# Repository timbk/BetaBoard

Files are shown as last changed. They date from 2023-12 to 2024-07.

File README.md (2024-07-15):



# BetaBoard

A particle detector built for cost-effectiveness when ordered at O(100) pieces.

The detector concept is adapted from the [DIY Particle Detector Project](https://github.com/ozel/DIY_particle_detector) by Oliver Keller.

## Hardware Revisions

| Revision 1 | Revision 2 |
| :---: | :---: |
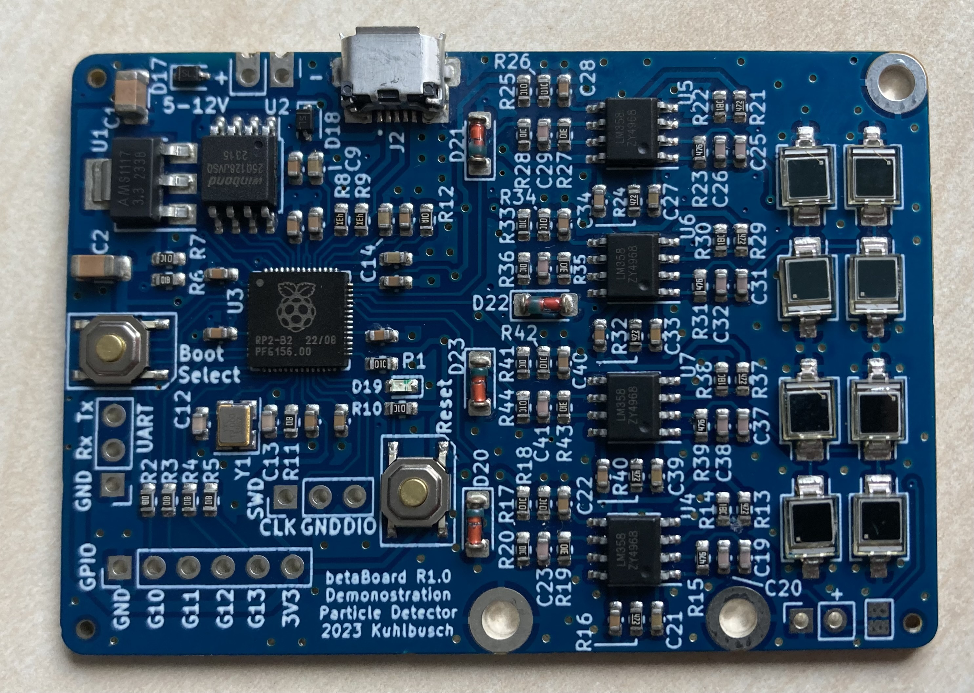
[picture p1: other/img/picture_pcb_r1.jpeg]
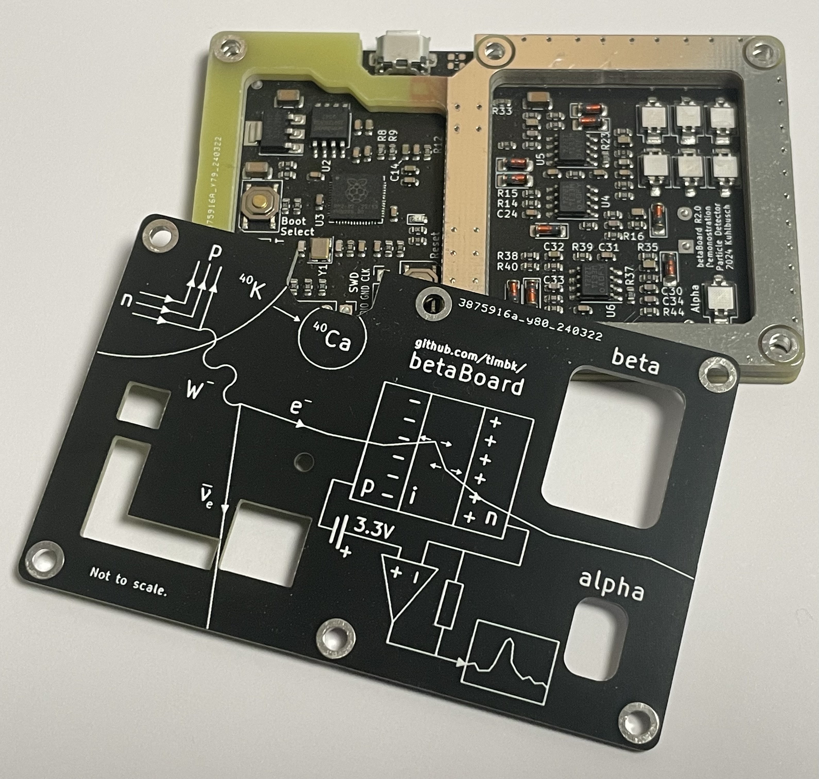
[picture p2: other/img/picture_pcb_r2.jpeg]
|  |  |
| [Schematic](hardware/betaBoard_r1.0/pdf/betaBoard_sch.pdf) [Layout](hardware/betaBoard_r1.0/pdf/betaBoard_pdf.pdf) | [Schematic](hardware/betaBoard_r2.0/betaBoard_r2.0_sch.pdf) [Layout](hardware/betaBoard_r2.0/betaBoard_r2.0_pcb.pdf) [Component Positions](hardware/betaBoard_r2.0/betaBoard_r2.0_positions.pdf) |
| Initial protoype: Working with adjustemtns to a few component values. Requires a lot of electrical and conductive tape to assemble. Designed for 16 diodes with the option to measure coincidences. | Streamlined redesign. Mainly adding a PCB casing to block light and radio imission. Attempting to add a simple alpha particle detector channel by stripping the isolation off of a diode (not successfull yet). Single channel with 6 diodes in parallel. Using additional ADC channels with less gain for debugging and potential experiments with scintillators. |

## Experiment Ideas

* Time distribution of pulses
* Rate vs distance (1/d^2 + offset)
* Absorption coefficient
    * Increase material thickness between detector and source
* Spectroscopy?? (alphas, sand down diode?
* Balloon in cellar

## Serial interface

* `T` `T <block_index> <timestamp_us> <overflow> # <sample_0> <sample_1> .. <sample_N>`
    * `block_index`: uint16_t, mainly relevant for debugging
    * `timestamp_us`: uint64_t, Trigger point timestamp in micro seconds since start of the measurement
    * `overflow`: bool, set to 1 if an overflow happend prior to this sample
    * `sample_n`:  int16_t, samples from the triggered waveform

## PCB

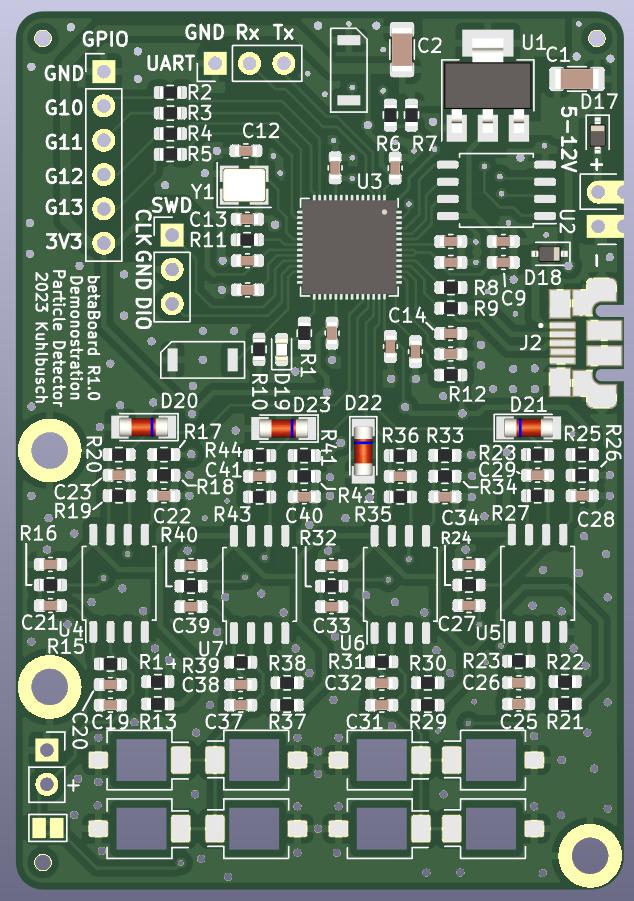
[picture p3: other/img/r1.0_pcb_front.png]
PCB front view

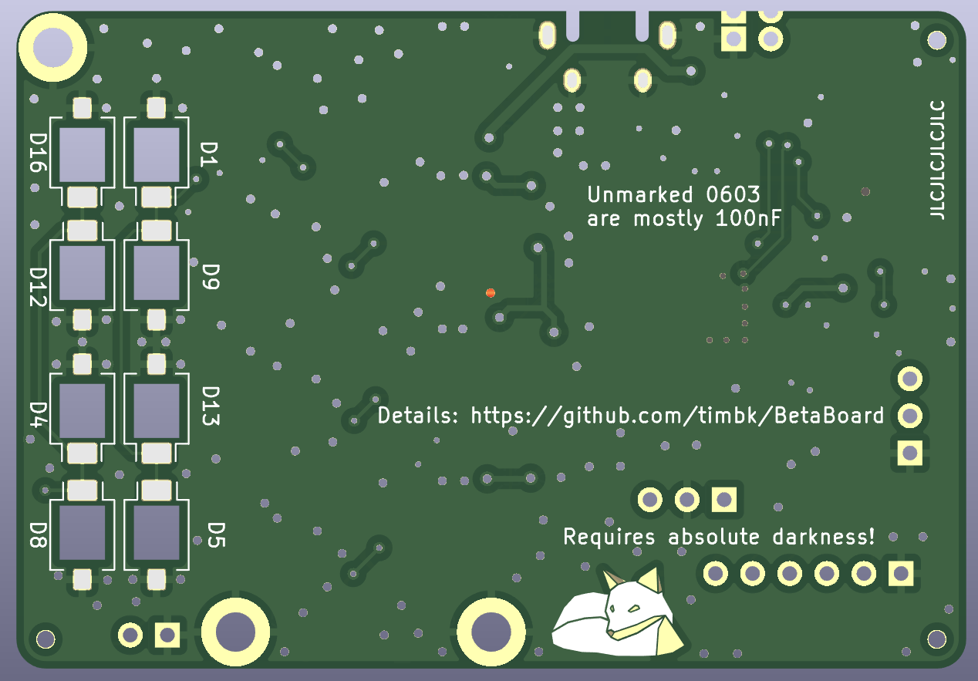
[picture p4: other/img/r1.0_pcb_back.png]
PCB back view


[Schematic](betaBoard/pdf/betaBoard_sch.pdf)
[Layout](betaBoard/pdf/betaBoard_pdf.pdf)

The goal was to keep it small to keep the PCB cost low and to make it fit easily.
Components were chosen to keep the price low and based on availablility at the chosen manufacturer.

## Ideas

* Strip detector with 4 pixels?
* File down SMD LEDs for less absorption?
* 3D-Printed Case?
* Interconnect multiple detectors?

## R2.0 ideas

* Put VCC on interconnect instead of 3V3
* Review diode cutout size
* Increase power supply castellated hole distance
* Increase LDO heat sink plane size
* Think about how usefull the coincidence concept is: 2x2 = 2+2 = 4!
* Silk to highlight Diode grouping
* Seperate bulk capacitor on 5V rail for analog

## Noise calculations

* Spice simulation: peak of ca. 40 $\mu\text{V}/\sqrt{\text{Hz}}$
    * Resistor thermal noise: $\sqrt{4k_BTR}\approx 400 ~ \text{nV/}\sqrt{\text{Hz}}$
    * LM358 input noise is ca. 40 $\text{nV}/\sqrt{\text{Hz}}$
    * Gain of second stage is ca. 100 for the peak frequency
    * => Resistor thermal noise is dominant part in simulation, LM385 noise should be negligible
        * $100 \cdot 400~\text{nV}/\sqrt{\text{Hz}} \approx 40~\mu\text{V}/\sqrt{\text{Hz}}$

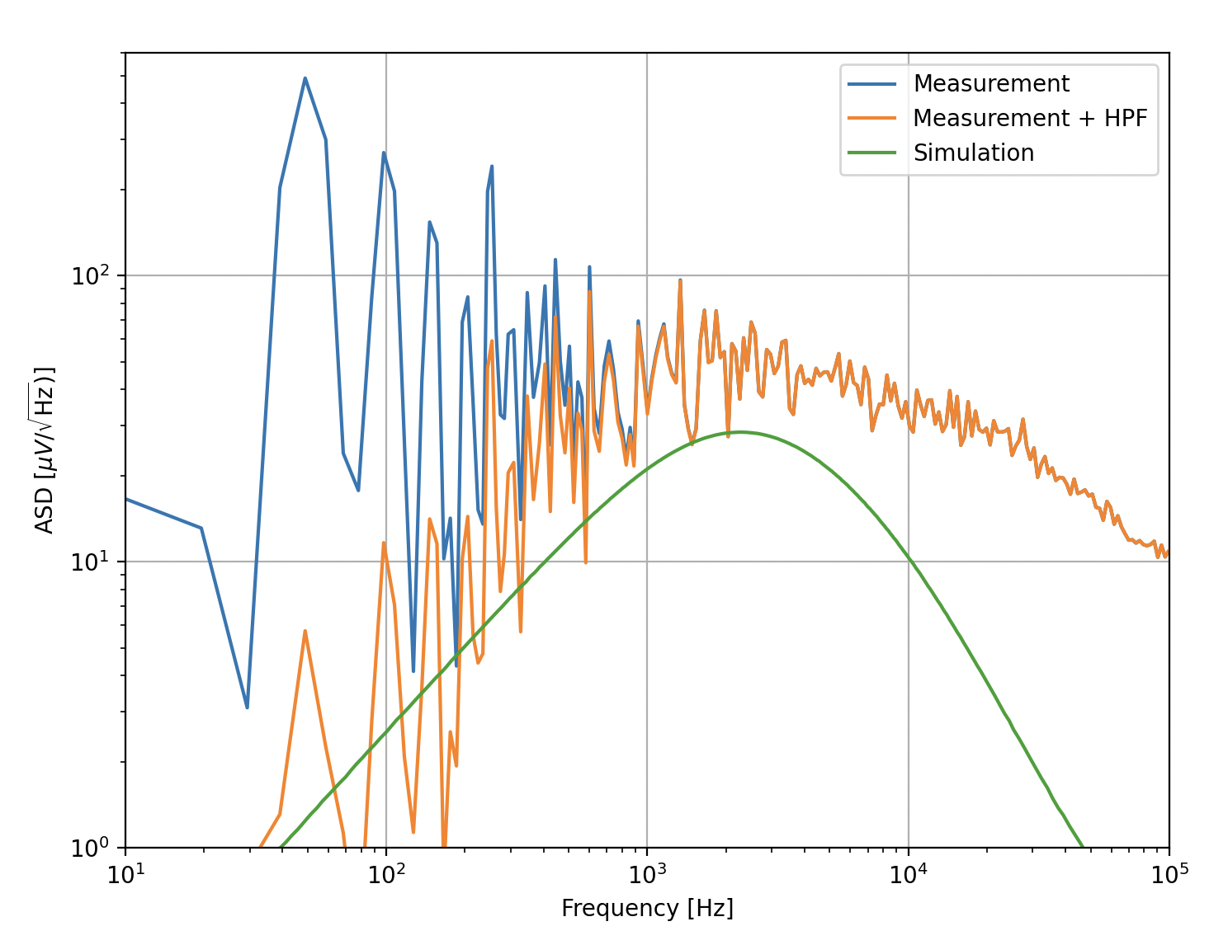
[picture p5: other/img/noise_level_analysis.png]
Noise plot


## Potential signal sources

* 10g KCl has ca. 164 Bq.
* Estimate of geometric acceptency at 2 cm distance: $A = \frac{4 \cdot 7.5~\text{mm}^2} {4\pi\cdot (20~\text{mm})^2} \approx 0.006$
    * With perfect efficiency: ca. 1 Hz

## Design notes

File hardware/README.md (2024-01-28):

# Hardware Files

## betaBoard.pretty

Custom KiCad footprints.

## betaBoard_r1.0

First revision of the PCB.

Design concepts:
* 4 Channels
    * adding channles came without significant cost (only opamps and passives)
    * 2 Channel on the back are expensive to populate
* Header to connect PD with leads
* External power header for up to 12 V to increase diode bias
* RP2040 allows simple programming via USB
    * Can be done by the user without special tools
* Allow options for different diode placement
    * More diodes yield more sensitivity

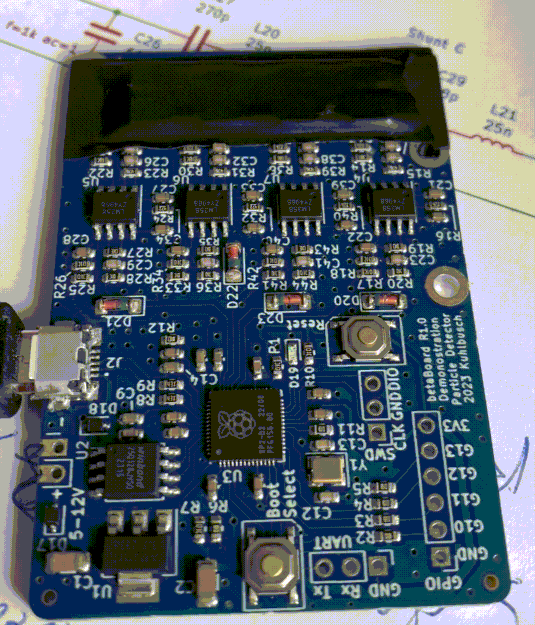
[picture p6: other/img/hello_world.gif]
PCB first LED blinking


Good:
* MCU, buttons, USB etc work perfectly out of the box :D

Challenges:
* High USB noise (1kHz spikes)
    * R14 requires a parallel C to get rid of noise from USB line
        * 1uF seems to help but does not seem sufficient (Could try 10uF, have 0603)
        * could increase R by factor 10
    * Try larger bulk capacitance (100uF or 1000uF)
        * 1000 uF seems to help!
        * Might be change in current draw
        * Cable length (resistance) seems to have an effect
    * Useing seperate diodes for the two supplies could help (diode voltage drop might depend on current)
    * TODO: Try if battery operation is better (helps to exclude potential points where 1 kHz noise couples)
* Is 40 MOhm working with the input impedance of LM358??
* Cut up groundplane at the PDs is probably not optimal
* Keep loop areas even smaller (I don't think it's the source of issues, but would feel better)
* USB port shielding is connected to GND. This might not be the optimal solution
    * Next: Add 2 0603 footprints? (allows open, short, 1MOhm+C)

## betaBoard_r1.1

Next revision. Work in progress.

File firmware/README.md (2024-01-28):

# RP2040 Firmware

## Build instructions

Requires a working installation of the [pico sdk](https://github.com/raspberrypi/pico-sdk).

```bash
cd firmware/
./build.sh
```

## Flashing

* Option 1: (simple)
> Hold the boot select pin on the PCB while connecting the board via USB. It will show up as a mass storage device. Copy `firmware/build/betaBoard.uf2` with a file manager (Finder/Explorer/..).

* Option 2: (complicated, but better for developement)
> Use a `picoprobe` and connect it to the SWD header. Execute the `./flash.sh` script.

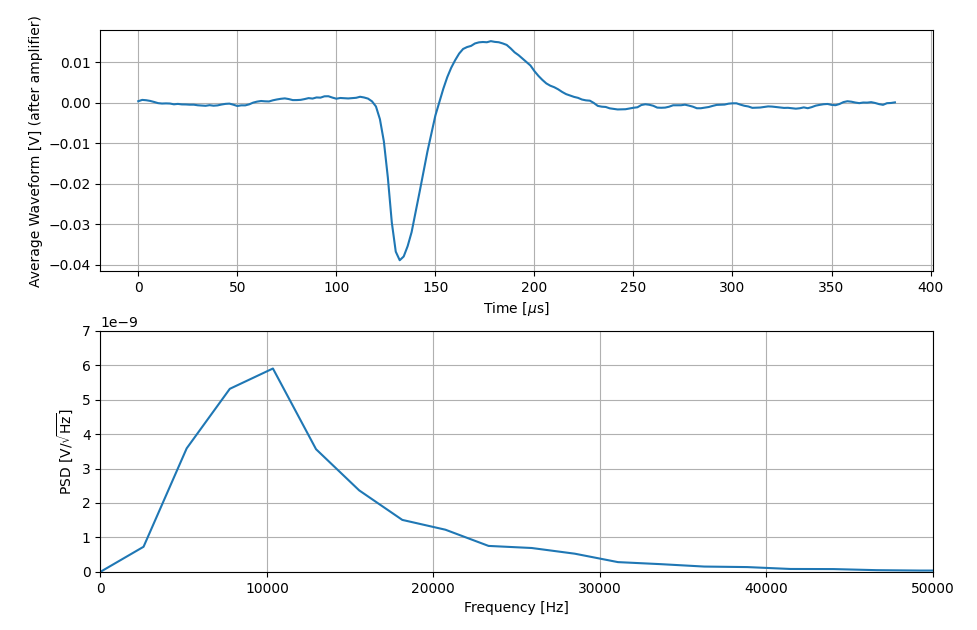
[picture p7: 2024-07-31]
other/img/avg_pulse_and_spectrum.png

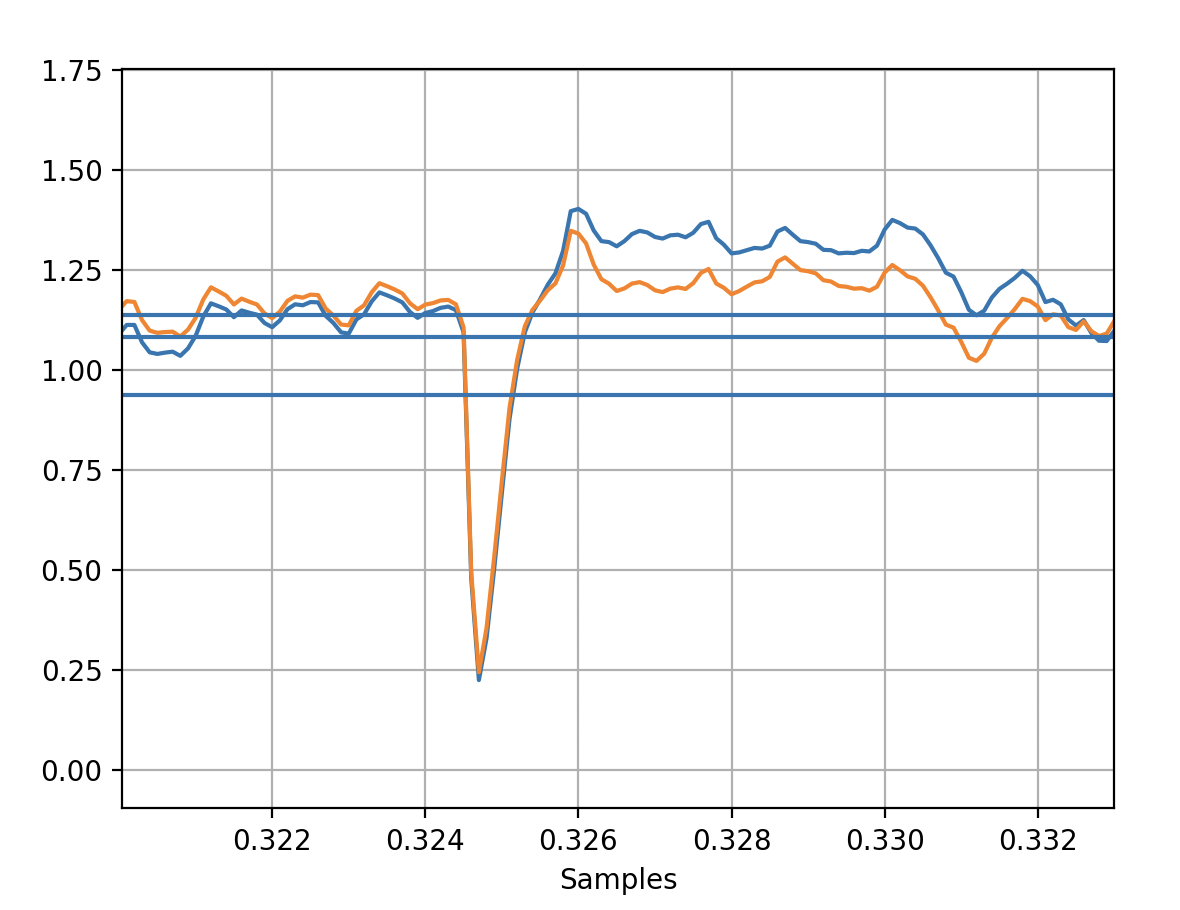
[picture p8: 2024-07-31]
other/img/first_pulse_maybe.png

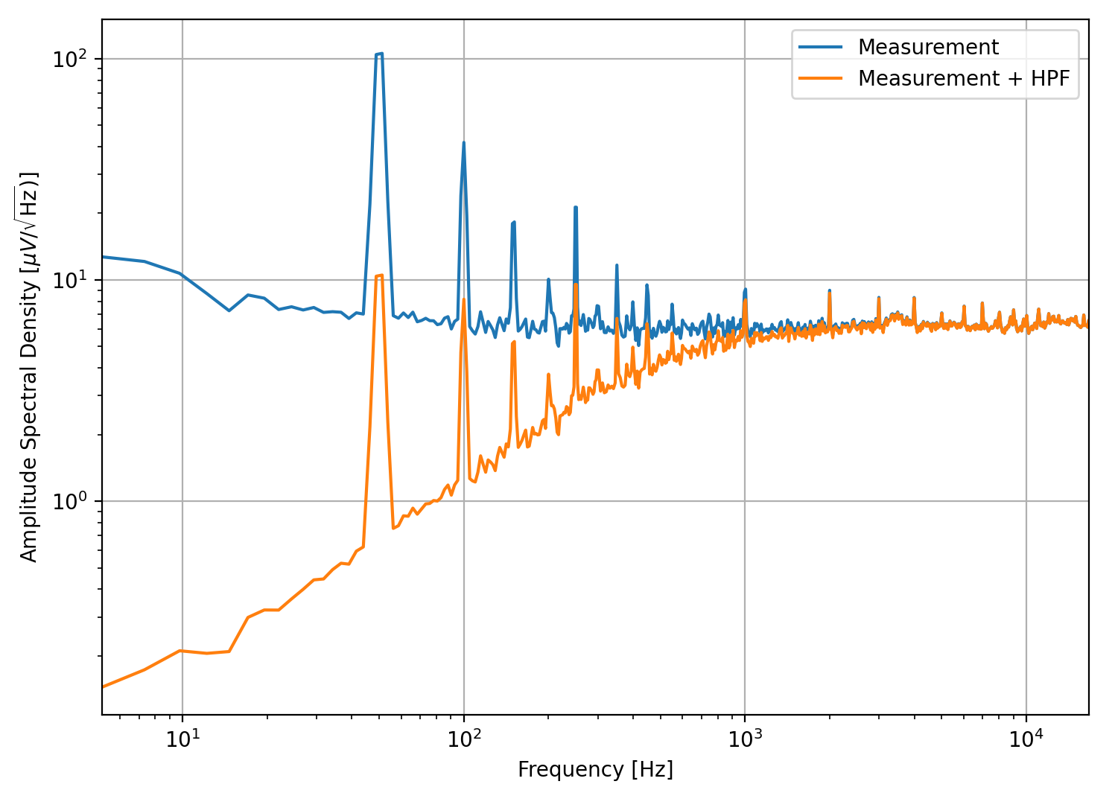
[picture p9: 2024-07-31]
other/img/noise_lpf.png

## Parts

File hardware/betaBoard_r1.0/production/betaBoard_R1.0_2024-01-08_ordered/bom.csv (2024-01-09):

Designator | Footprint | Quantity | Value | LCSC Part #
C1, C2 | 1206 | 2 | 10u
C10, C11, C15, C16, C18, C22, C24, C28, C3, C30, C34, C36, C4, C40, C5, C6, C7, C8 | 0603 | 18 | 100n
C12, C13 | 0603 | 2 | 30p
C14, C17, C9 | 0603 | 3 | 1u
C19, C20, C25, C26, C31, C32, C37, C38 | 0603 | 8 | 10p
C21, C27, C33, C39 | 0603 | 4 | 470n
C23, C29, C35, C41 | 0603 | 4 | 47p
D10, D11, D14, D15, D2, D3, D6, D7 | Osram_BPW34S-SMD_hole | 8 | BPW34-SMD
D17, D18 | D_SOD-323 | 2 | 1N5819WS
D19 | 0603 | 1 | LED
D20, D21, D22, D23 | D_MiniMELF | 4 | ZMM3V3-M
J2 | AMPHENOL_10103592-0001LF | 1 | AMPHENOL_10103592-0001LF
R1, R10, R17, R18, R20, R25, R26, R28, R33, R34, R36, R41, R42, R44, R7 | 0603 | 15 | 10k
R11, R2, R3, R4, R5, R6 | 0603 | 6 | 1k
R12 | 0603 | 1 | 100
R13, R16, R21, R24, R29, R32, R37, R40 | 0603 | 8 | 4k7
R14, R22, R30, R38 | 0603 | 4 | 15k
R15, R23, R31, R39 | 0603 | 4 | 47M
R19, R27, R35, R43 | 0603 | 4 | 1M
R8, R9 | 0603 | 2 | 27.4
SW1, SW2 | TS-1187A-B-A-B | 2 | C26638
U1 | SOT-223-3_TabPin2 | 1 | AMS1117-3.3_SOT223
U2 | SOIC-8_5.23x5.23mm_P1.27mm | 1 | W25Q128JVSIQ
U3 | QFN-56-1EP_7x7mm_P0.4mm_EP3.2x3.2mm | 1 | RP2040
U4, U5, U6, U7 | SOIC-8_3.9x4.9mm_P1.27mm | 4 | LM358
Y1 | Crystal_SMD_3225-4Pin_3.2x2.5mm | 1 | X322512MSB4SI

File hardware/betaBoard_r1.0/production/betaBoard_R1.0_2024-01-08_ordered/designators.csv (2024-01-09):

C1:1
C10:1
C11:1
C12:1
C13:1
C14:1
C15:1
C16:1
C17:1
C18:1
C19:1
C2:1
C20:1
C21:1
C22:1
C23:1
C24:1
C25:1
C26:1
C27:1
C28:1
C29:1
C3:1
C30:1
C31:1
C32:1
C33:1
C34:1
C35:1
C36:1
C37:1
C38:1
C39:1
C4:1
C40:1
C41:1
C5:1
C6:1
C7:1
C8:1
C9:1
D1:1
D10:1
D11:1
D12:1
D13:1
D14:1
D15:1
D16:1
D17:1
D18:1
D19:1
D2:1
D20:1
D21:1
D22:1
D23:1
D3:1
D4:1
D5:1
D6:1
D7:1
D8:1
D9:1
G***:1
H1:1
H2:1
H3:1
H4:1
H5:1
H6:1
J1:1
J2:1
J3:1
J4:1
J5:1
J6:1
JP1:1
R1:1
R10:1
R11:1
R12:1
R13:1
R14:1
R15:1
R16:1
R17:1
R18:1
R19:1
R2:1
R20:1
R21:1
R22:1
R23:1
R24:1
R25:1
R26:1
R27:1
R28:1
R29:1
R3:1
R30:1
R31:1
R32:1
R33:1
R34:1
R35:1
R36:1
R37:1
R38:1
R39:1
R4:1
R40:1
R41:1
R42:1
R43:1
R44:1
R5:1
R6:1
R7:1
R8:1
R9:1
SW1:1
SW2:1
U1:1
U2:1
U3:1
U4:1
U5:1
U6:1
U7:1
Y1:1

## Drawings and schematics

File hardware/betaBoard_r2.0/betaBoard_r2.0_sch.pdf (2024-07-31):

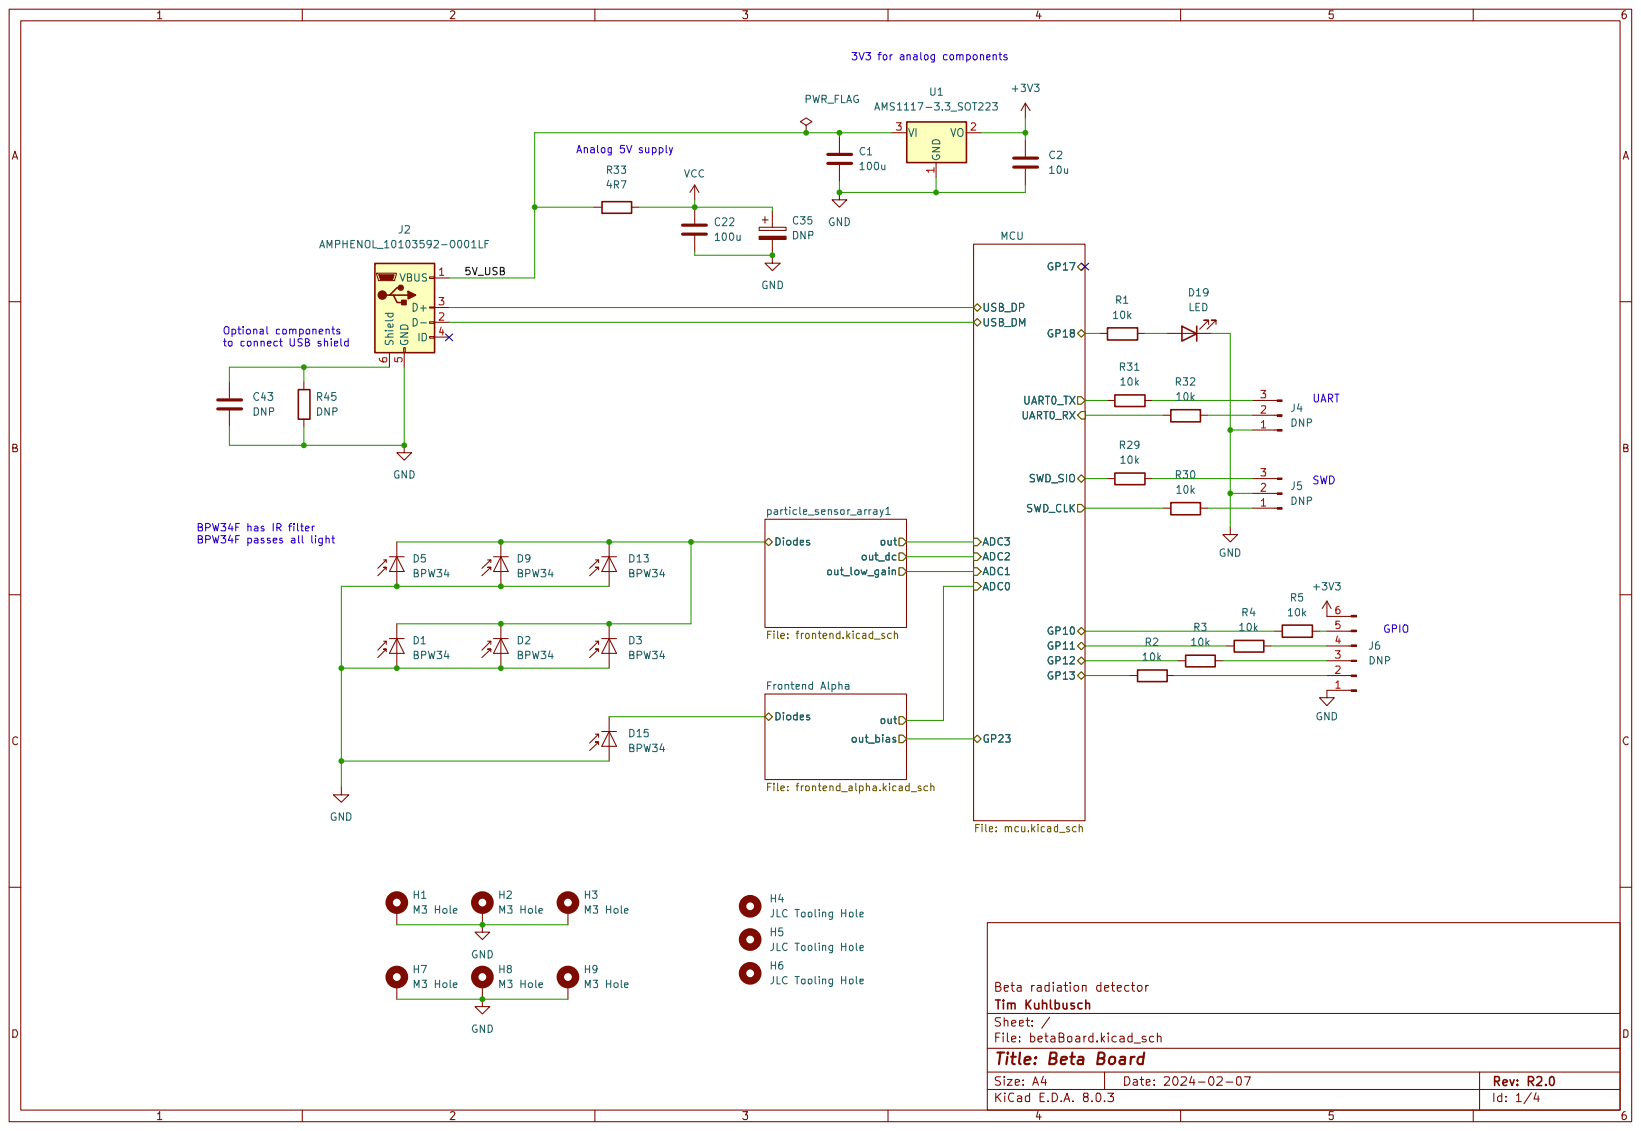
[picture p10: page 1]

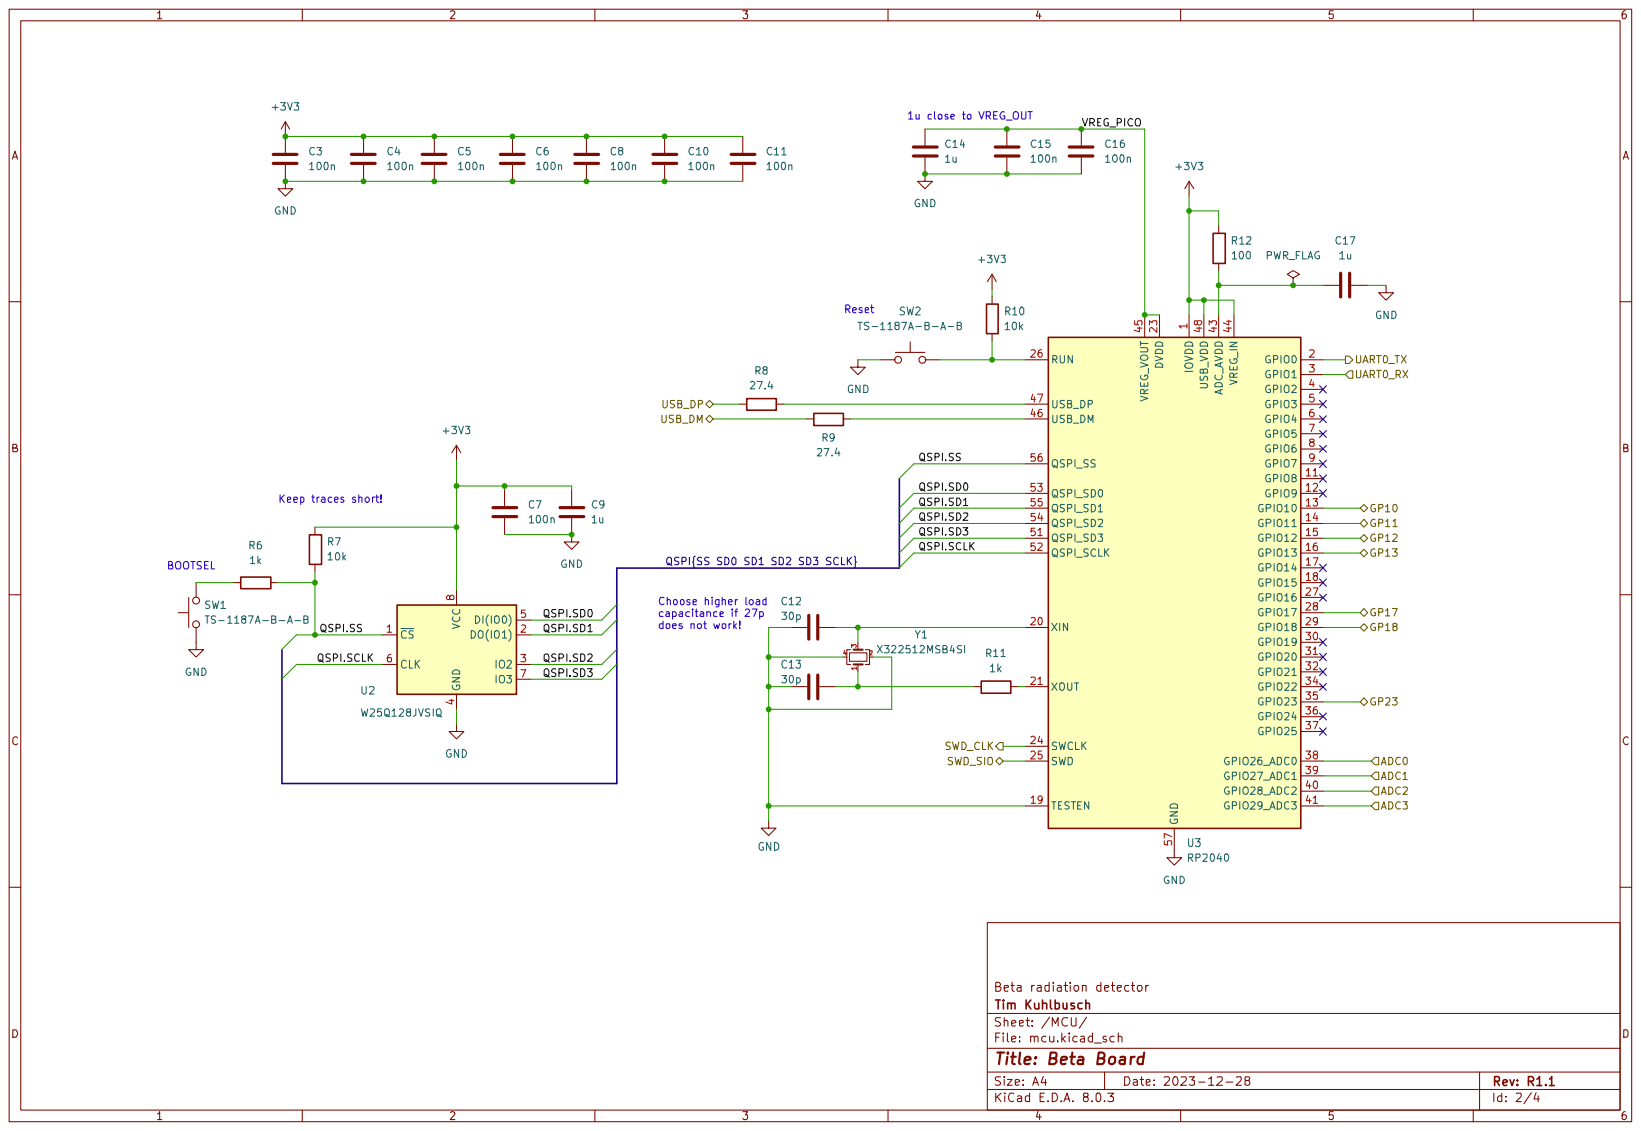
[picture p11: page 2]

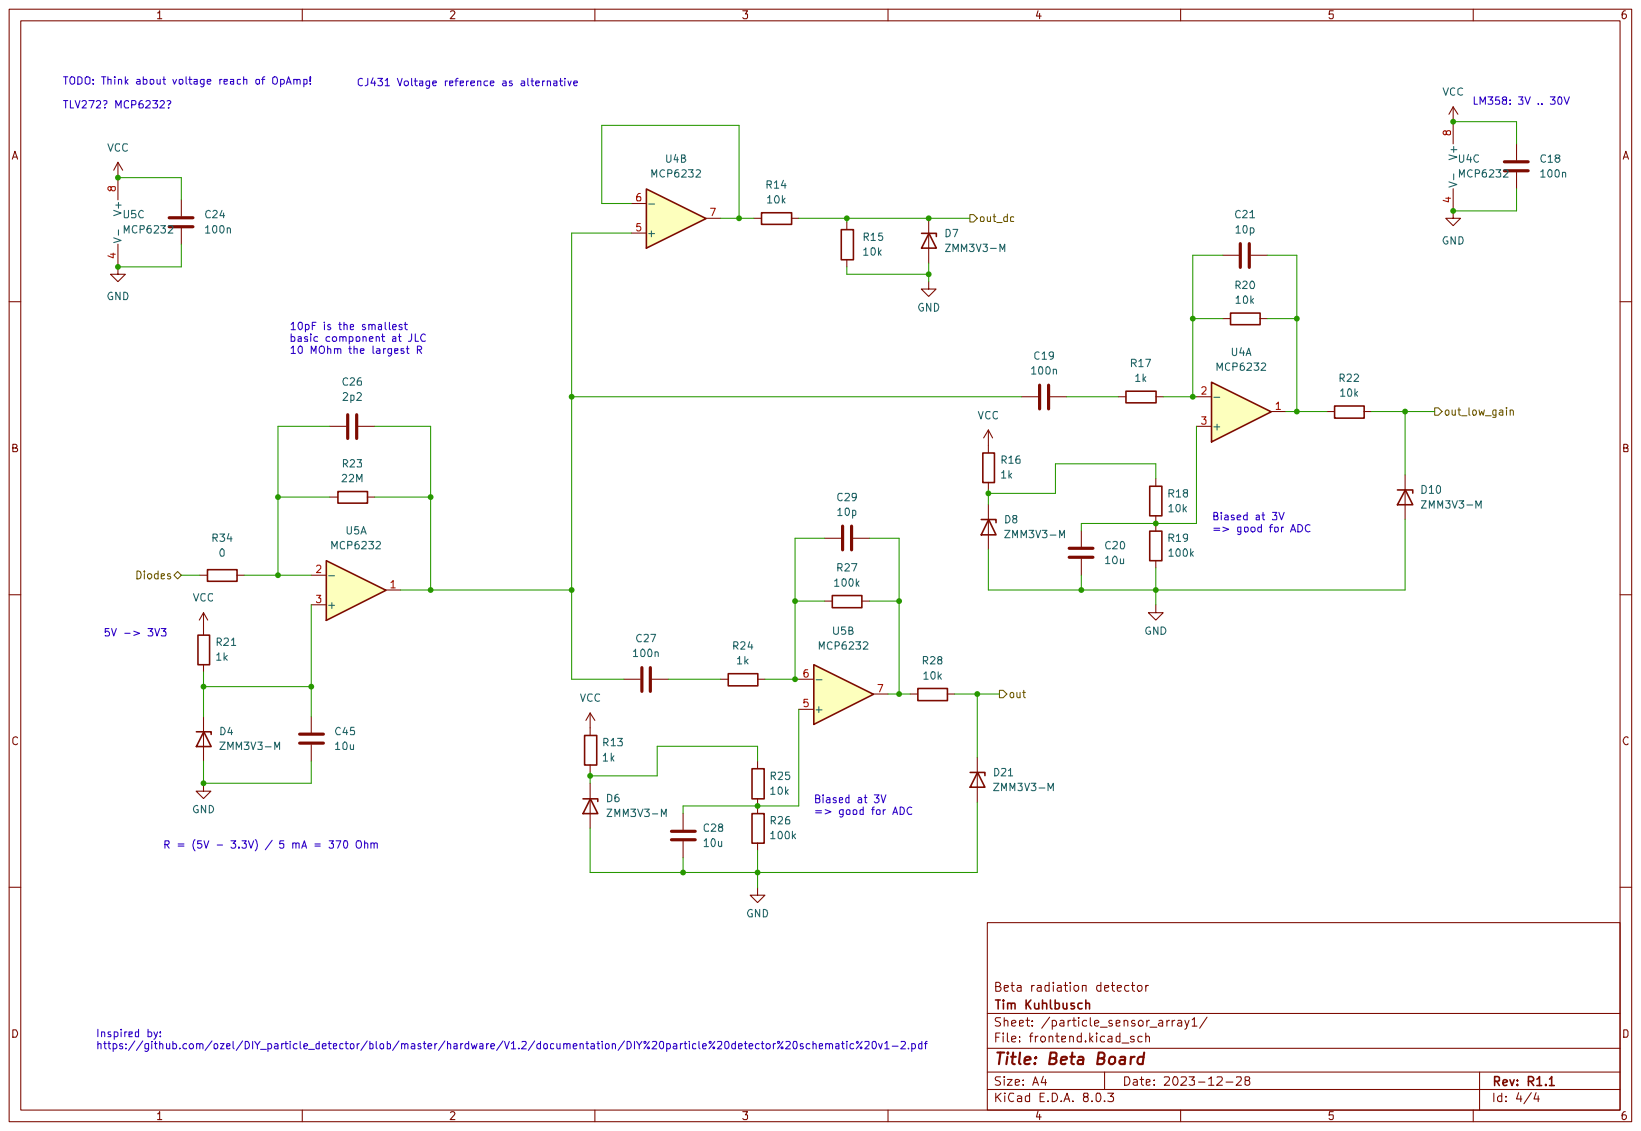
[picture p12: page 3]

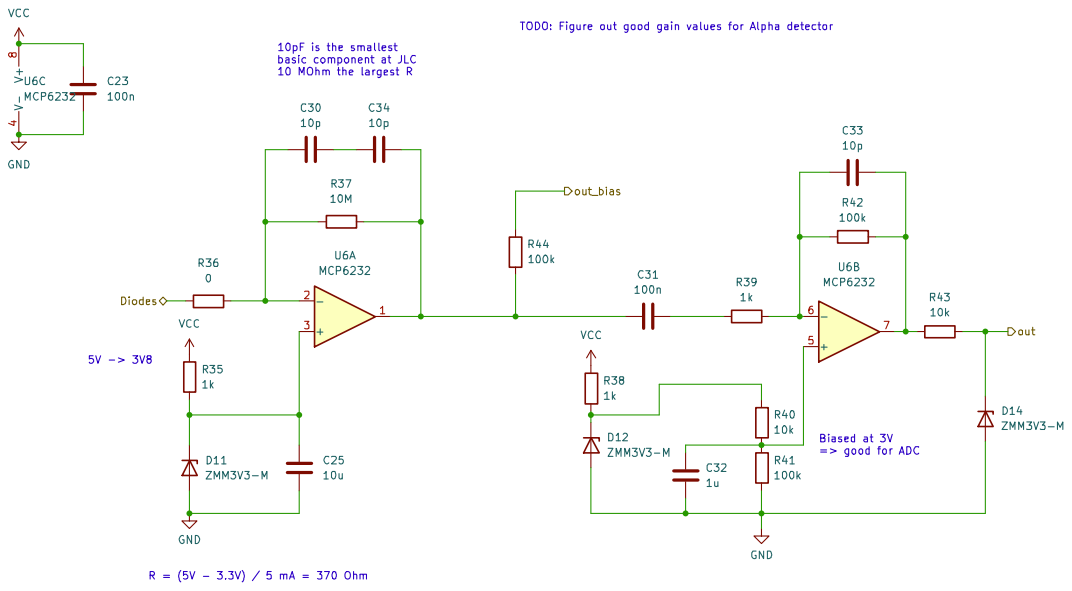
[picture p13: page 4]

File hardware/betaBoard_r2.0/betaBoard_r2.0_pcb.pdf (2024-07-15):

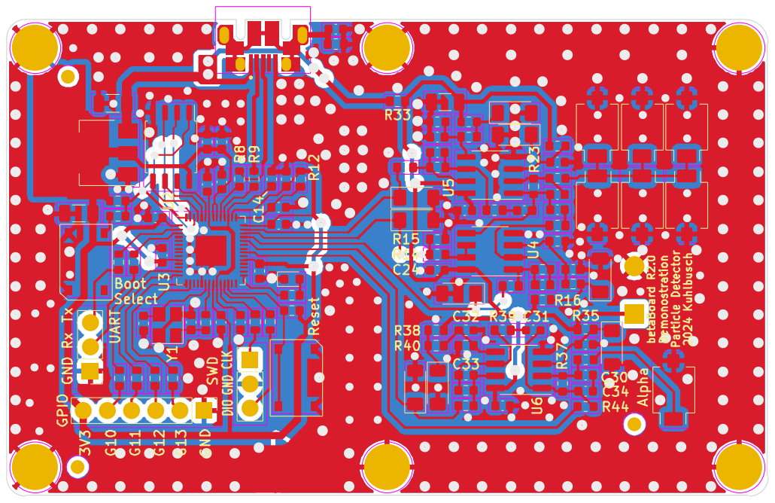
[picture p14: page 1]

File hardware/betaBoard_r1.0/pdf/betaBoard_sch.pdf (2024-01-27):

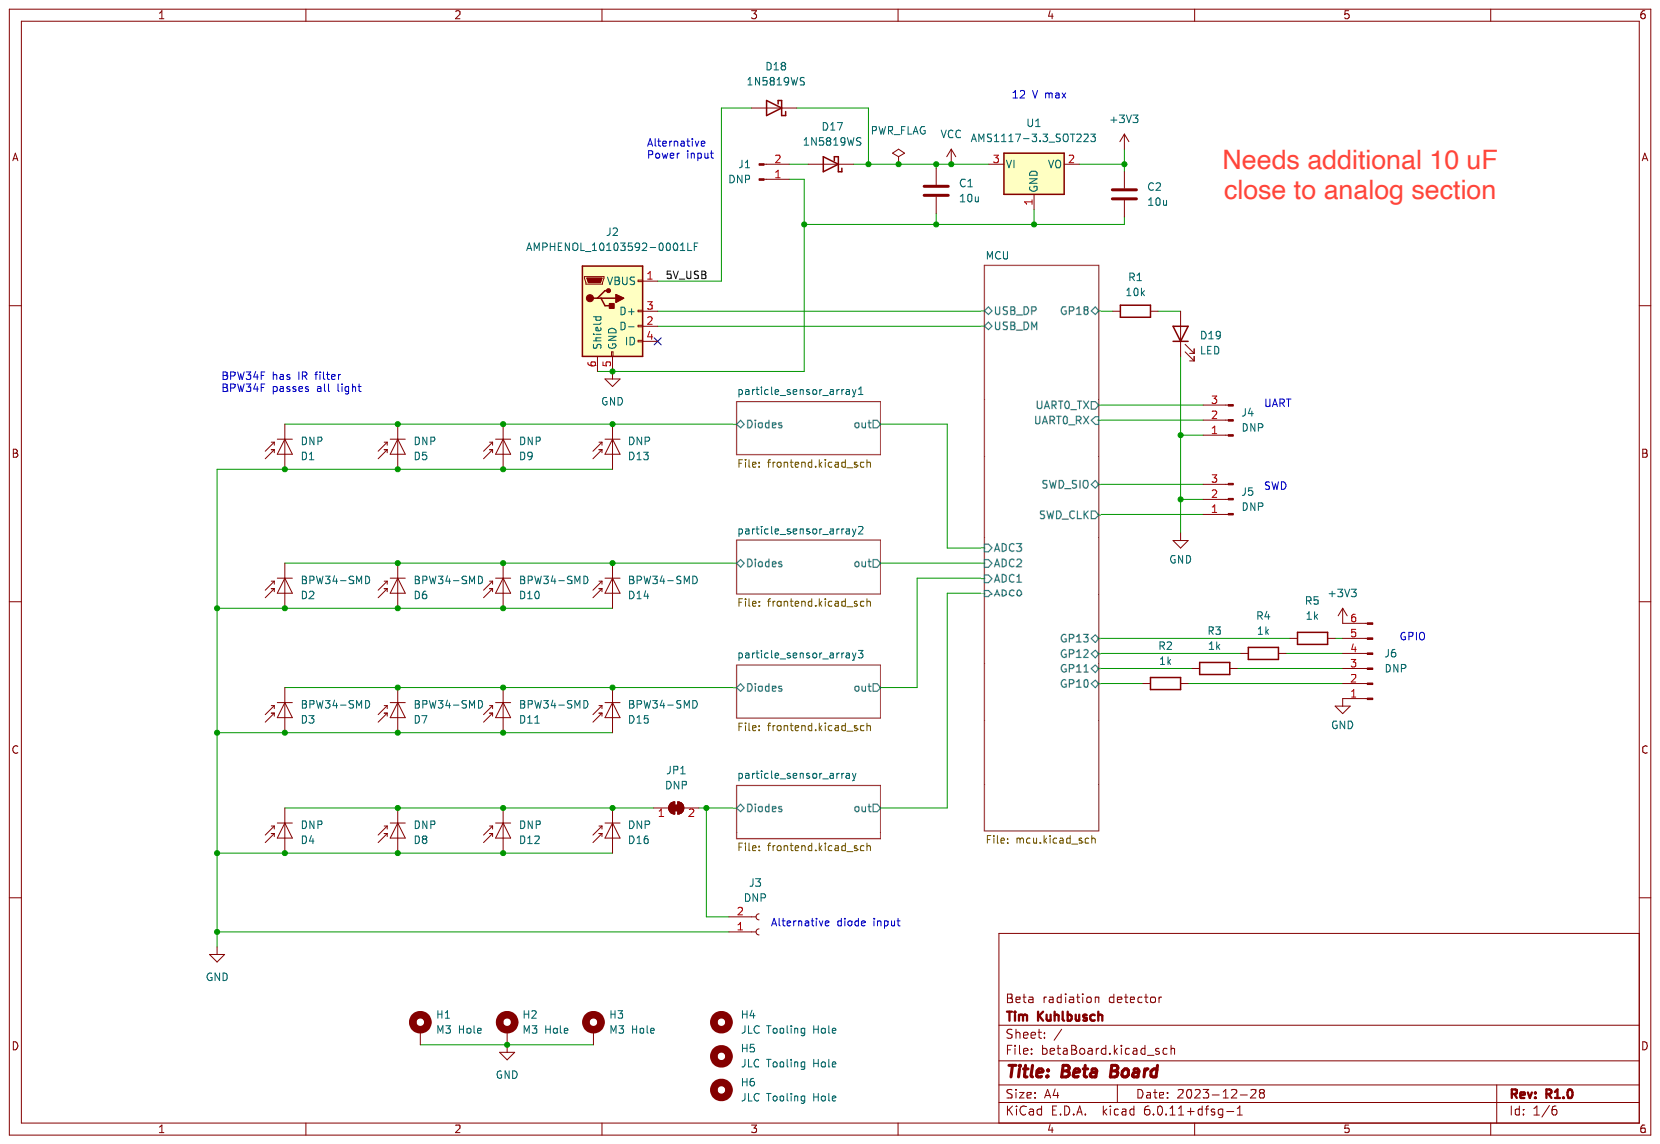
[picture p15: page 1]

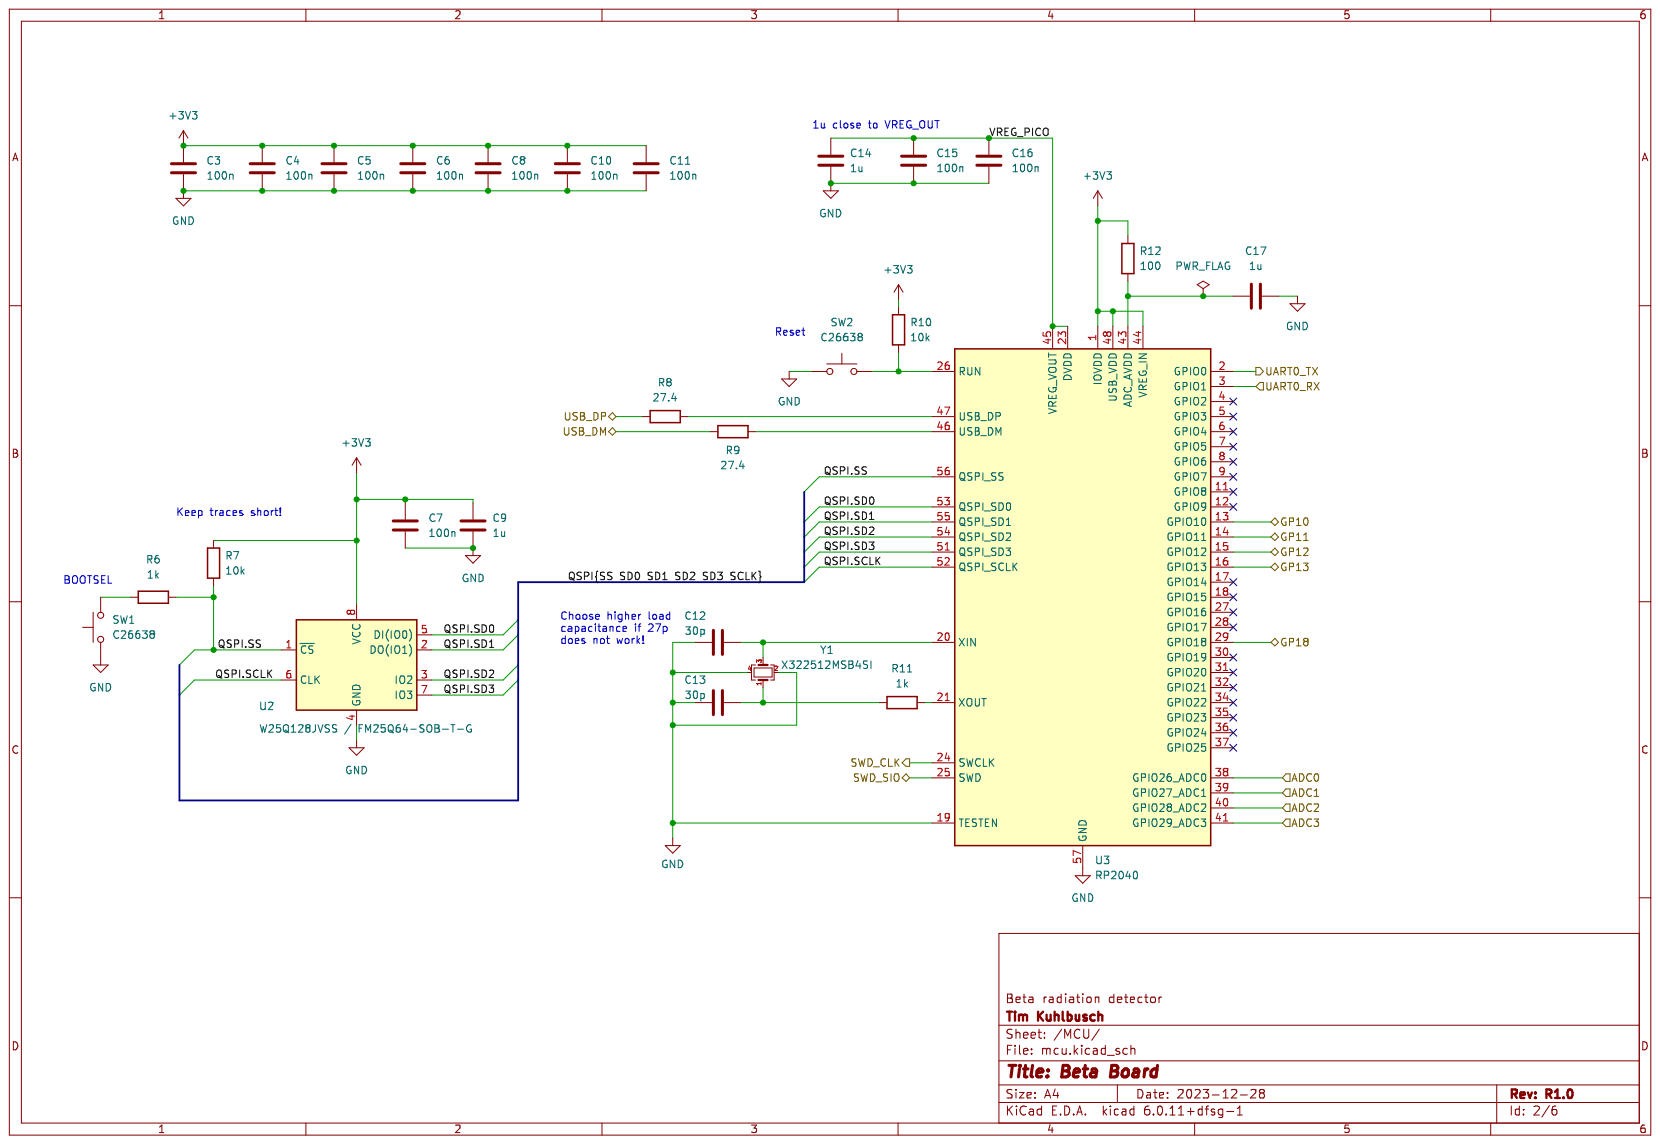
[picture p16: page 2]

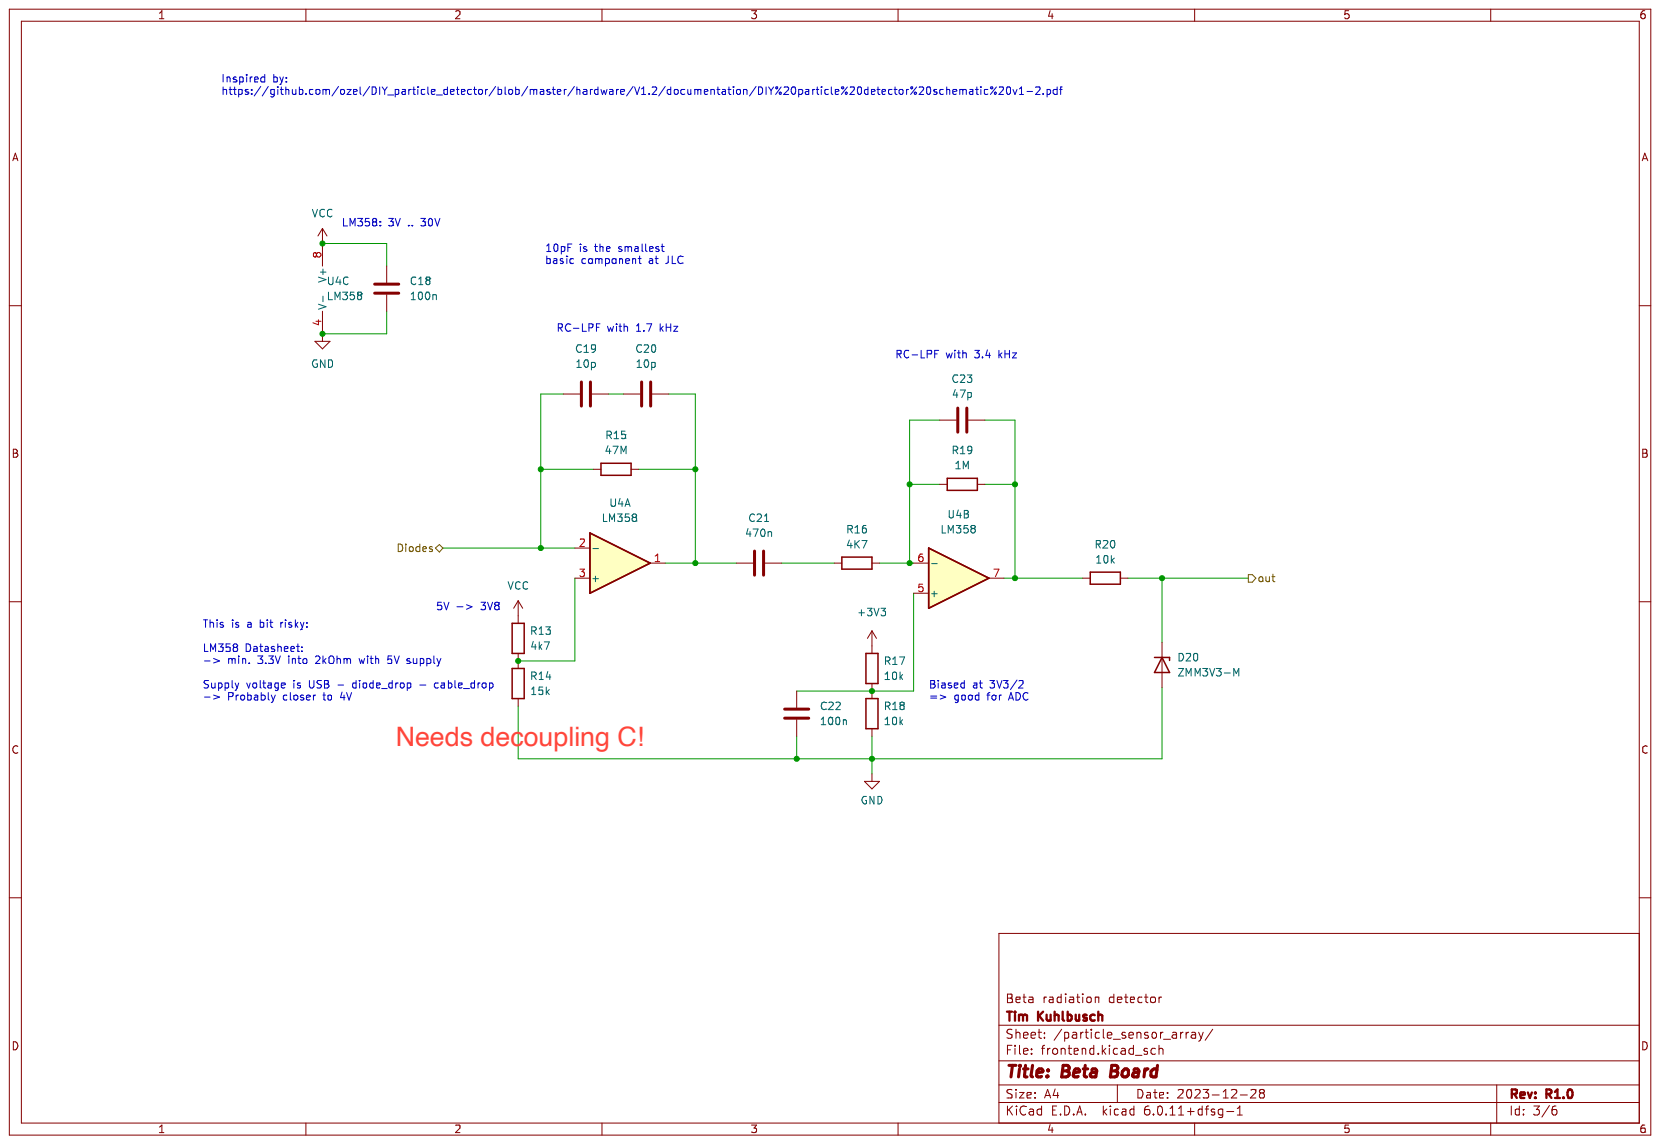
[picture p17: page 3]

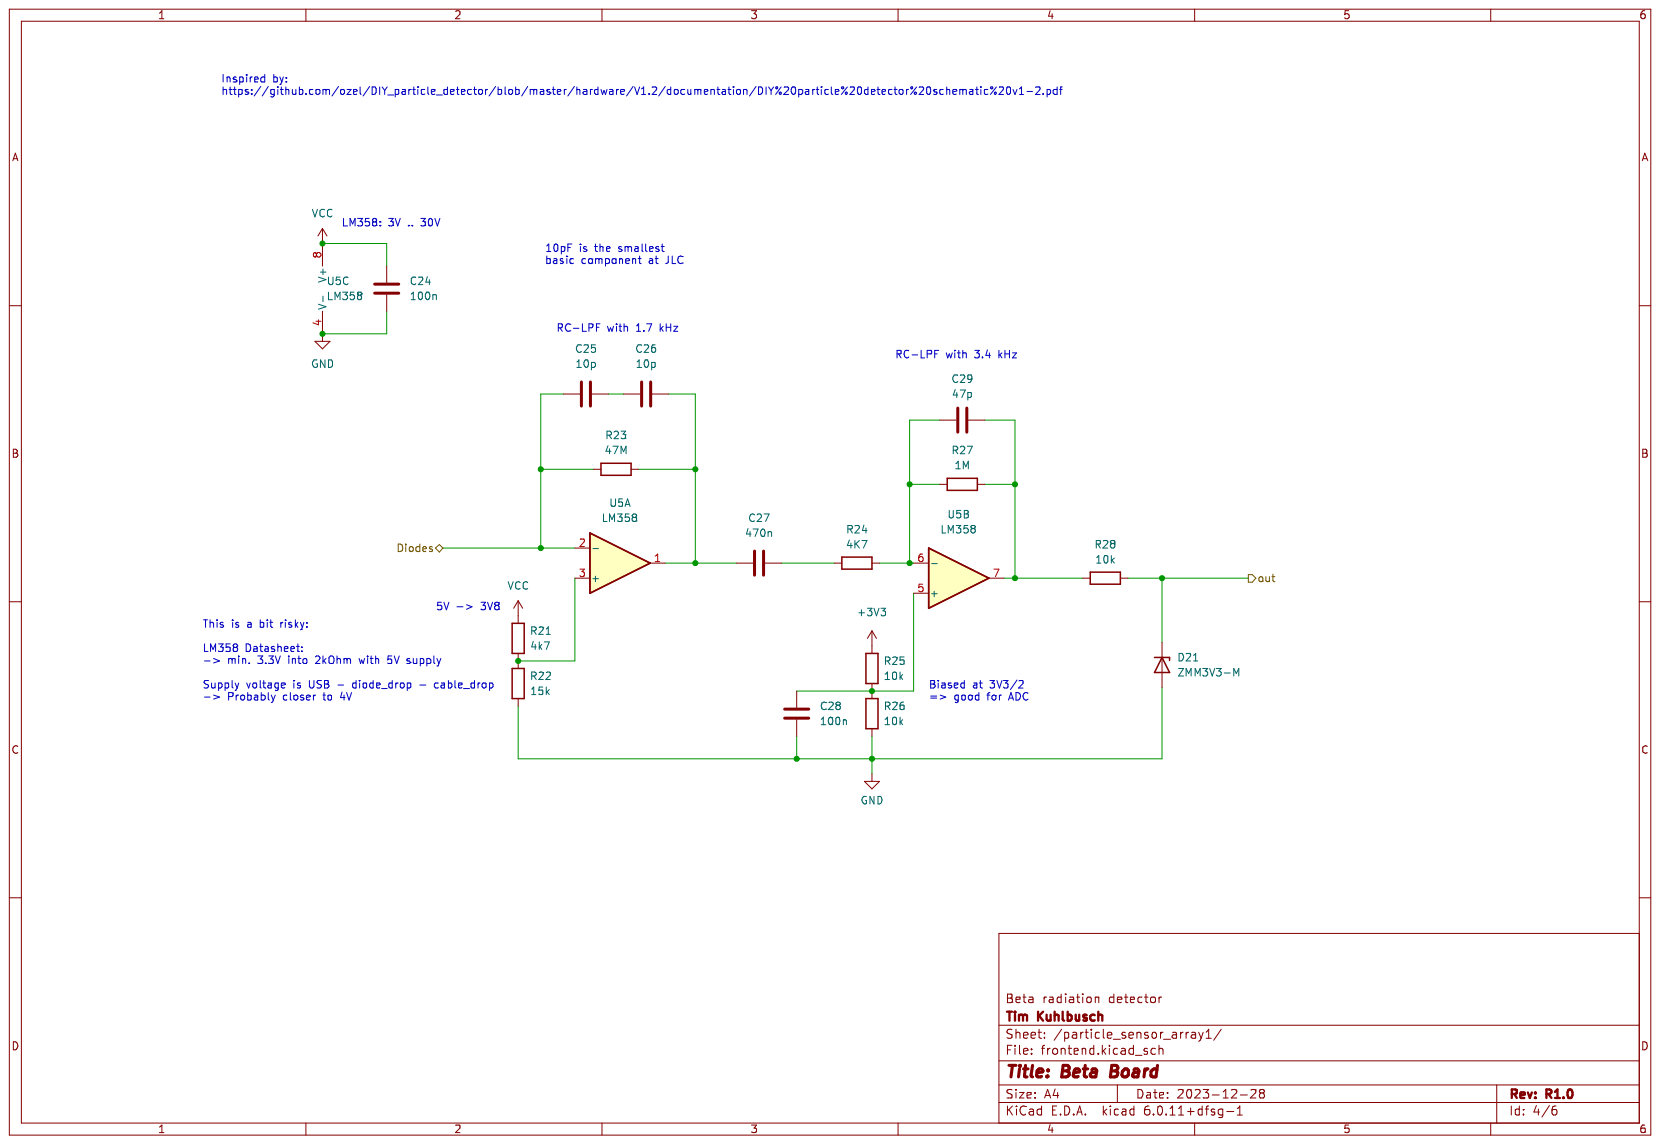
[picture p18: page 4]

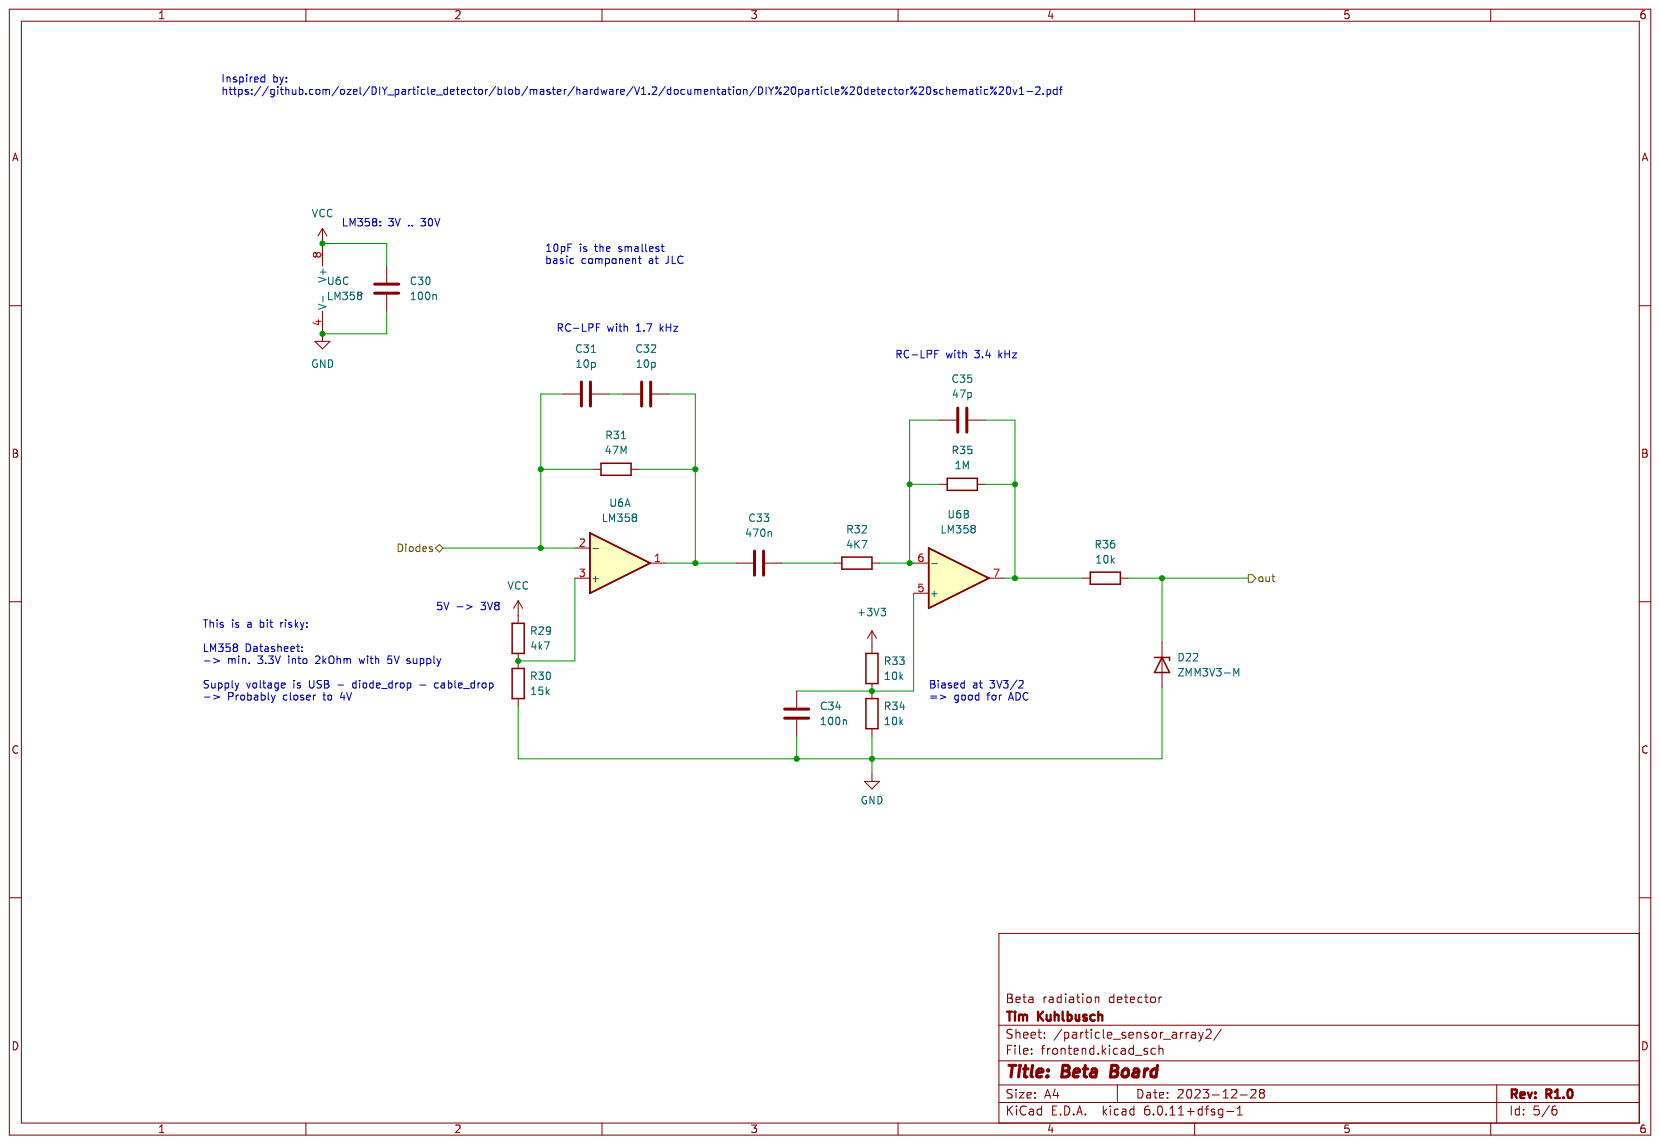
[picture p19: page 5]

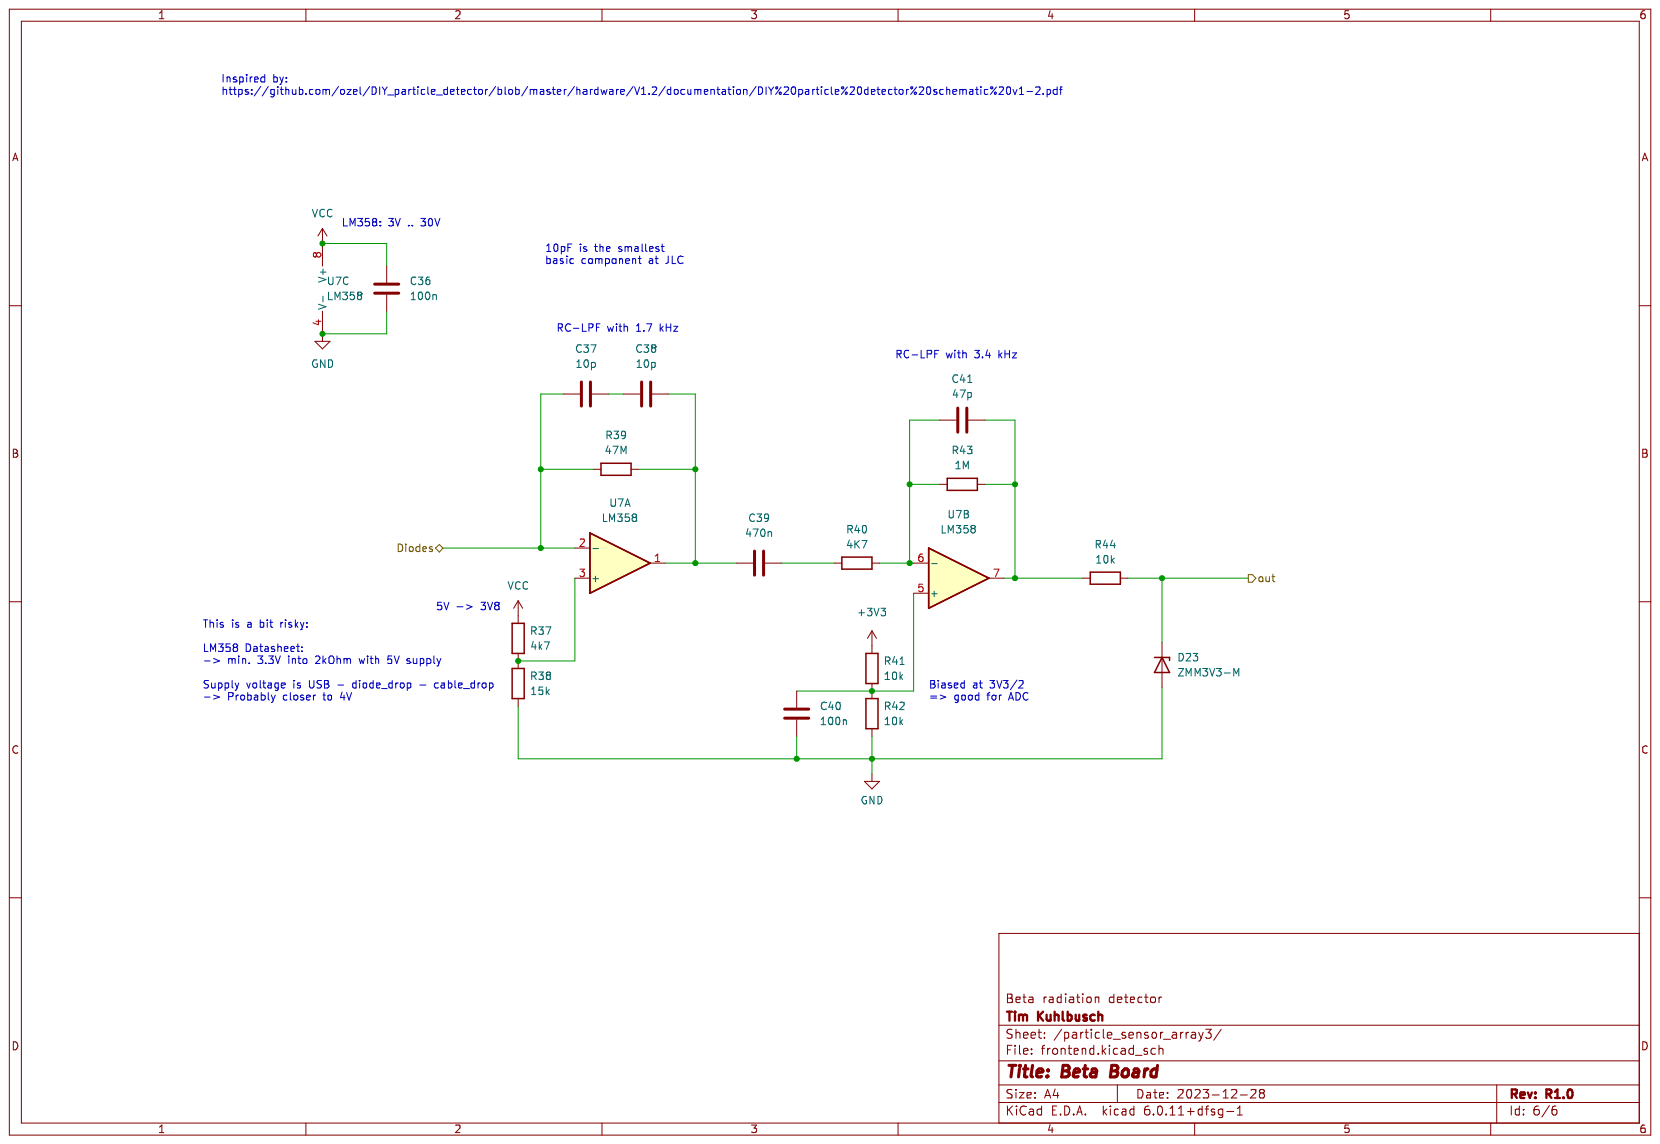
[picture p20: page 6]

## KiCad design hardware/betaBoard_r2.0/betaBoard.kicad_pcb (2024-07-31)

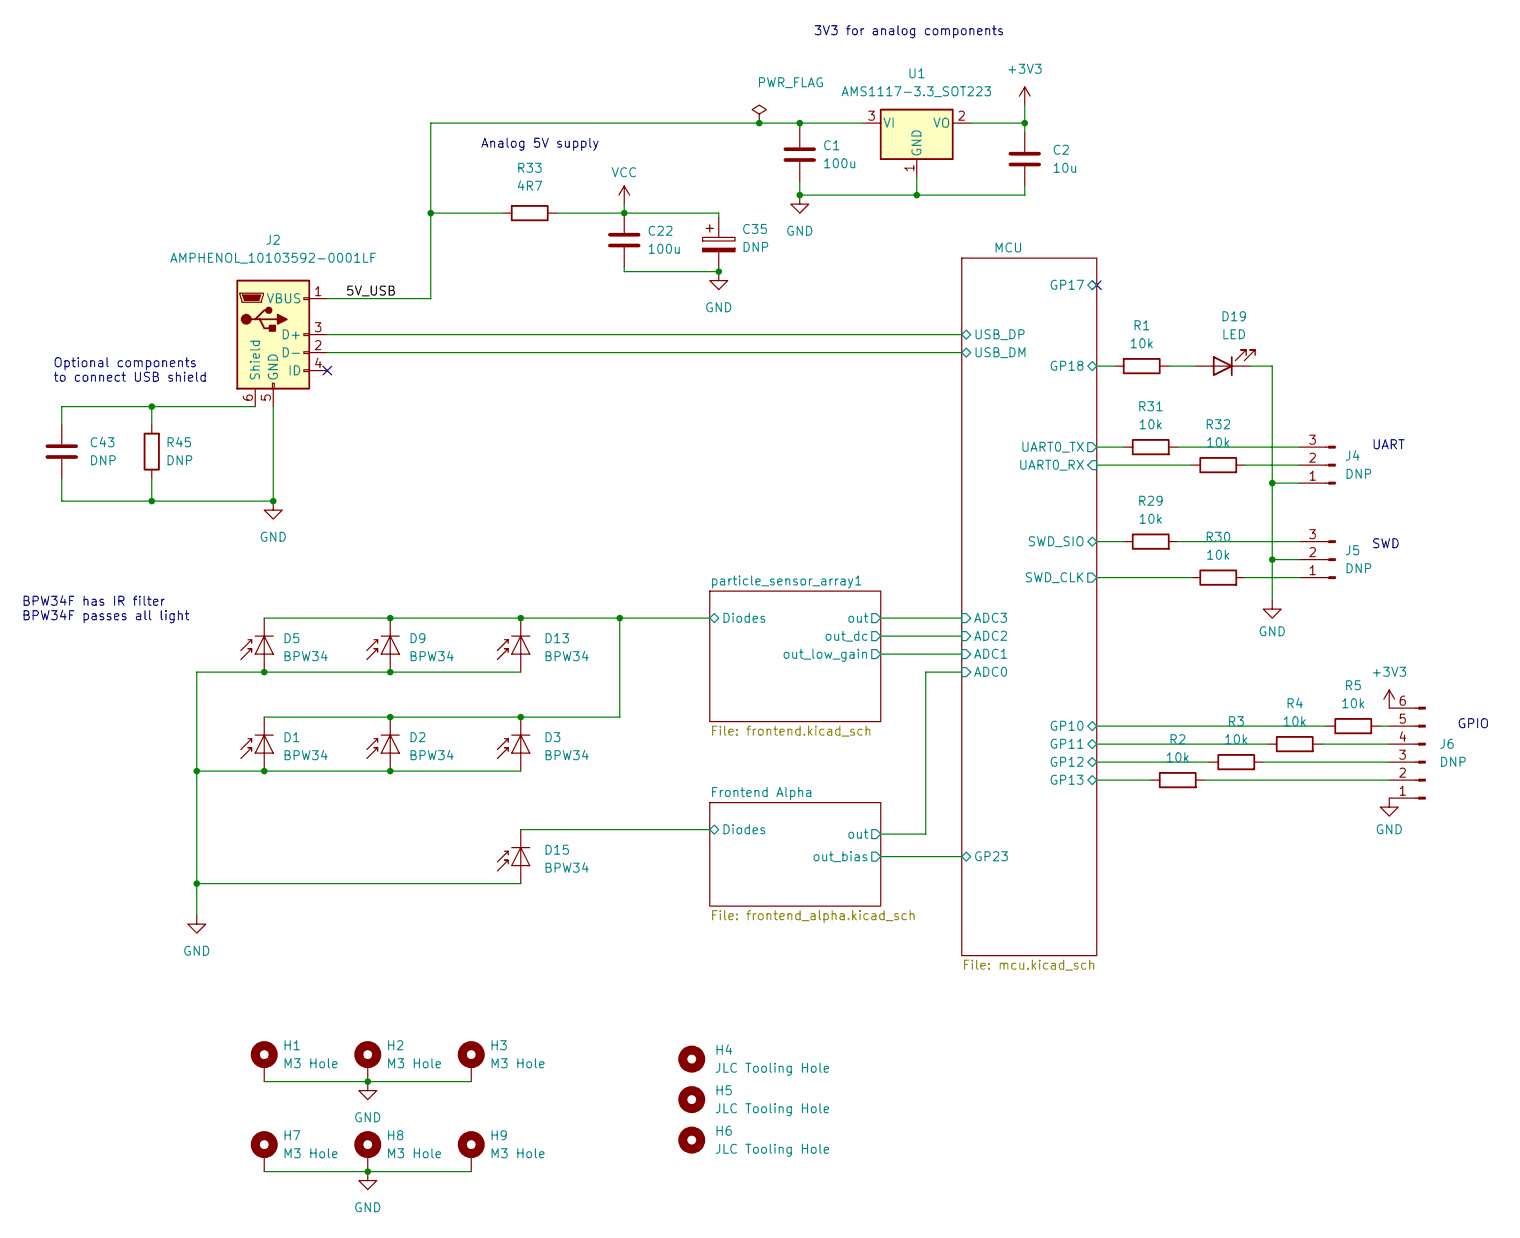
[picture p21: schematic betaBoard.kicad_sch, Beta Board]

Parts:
C1, C22: 100u; C_1206_3216Metric
C2: 10u; C_1206_3216Metric
C35: DNP; CP_Radial_D10.0mm_P5.00mm
C43: DNP; C_0603_1608Metric
D1, D2, D3, D5, D9, D13, D15: BPW34; Osram_BPW34S-SMD
D19: LED; LED_0603_1608Metric
H1, H2, H3, H7, H8, H9: M3 Hole; MountingHole_2.7mm_M2.5_DIN965_Pad
H4, H5, H6: JLC Tooling Hole; JLC_tooling_hole
J2: AMPHENOL_10103592-0001LF
J4, J5: DNP; PinHeader_1x03_P2.54mm_Vertical
J6: DNP; PinHeader_1x06_P2.54mm_Vertical
R1, R2, R3, R4, R5, R29, R30, R31, R32: 10k; R_0603_1608Metric
R33: 4R7; R_0603_1608Metric
R45: DNP; R_0603_1608Metric
U1: AMS1117-3.3_SOT223; SOT-223-3_TabPin2

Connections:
+3V3: C2.1, J6.6, U1.2 (VO); also elsewhere on the board
/5V_USB: C1.1, J2.1 (VBUS), R33.2, U1.3 (VI)
/Frontend Alpha/Diodes: D15.1 (K); also elsewhere on the board
/MCU/GP10: R5.1; also elsewhere on the board
/MCU/GP11: R4.1; also elsewhere on the board
/MCU/GP12: R3.1; also elsewhere on the board
/MCU/GP13: R2.1; also elsewhere on the board
/MCU/GP18: R1.2; also elsewhere on the board
/MCU/SWD_CLK: R30.1; also elsewhere on the board
/MCU/SWD_SIO: R29.1; also elsewhere on the board
/MCU/UART0_RX: R32.1; also elsewhere on the board
/MCU/UART0_TX: R31.1; also elsewhere on the board
/MCU/USB_DM: J2.2 (D-); also elsewhere on the board
/MCU/USB_DP: J2.3 (D+); also elsewhere on the board
/particle_sensor_array1/Diodes: D1.1 (K), D2.1 (K), D3.1 (K), D5.1 (K), D9.1 (K), D13.1 (K); also elsewhere on the board
GND: C1.2, C2.2, C22.2, C35.2, C43.2, D1.2 (A), D2.2 (A), D3.2 (A), D5.2 (A), D9.2 (A), D13.2 (A), D15.2 (A), D19.1 (K), H1.1, H2.1, H3.1, H7.1, H8.1, H9.1, J2.5 (GND), J4.1, J5.2, J6.1, R45.1, U1.1 (GND); also elsewhere on the board
unnamed: D19.2 (A), R1.1
unnamed: C43.1, J2.6 (Shield), R45.2
unnamed: J4.2, R32.2
unnamed: J4.3, R31.2
unnamed: J5.1, R30.2
unnamed: J5.3, R29.2
unnamed: J6.2, R2.2
unnamed: J6.3, R3.2
unnamed: J6.4, R4.2
unnamed: J6.5, R5.2
VCC: C22.1, C35.1, R33.1; also elsewhere on the board

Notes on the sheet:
SWD
GPIO
Analog 5V supply
3V3 for analog components
BPW34F has IR filter BPW34F passes all light
UART
Optional components to connect USB shield

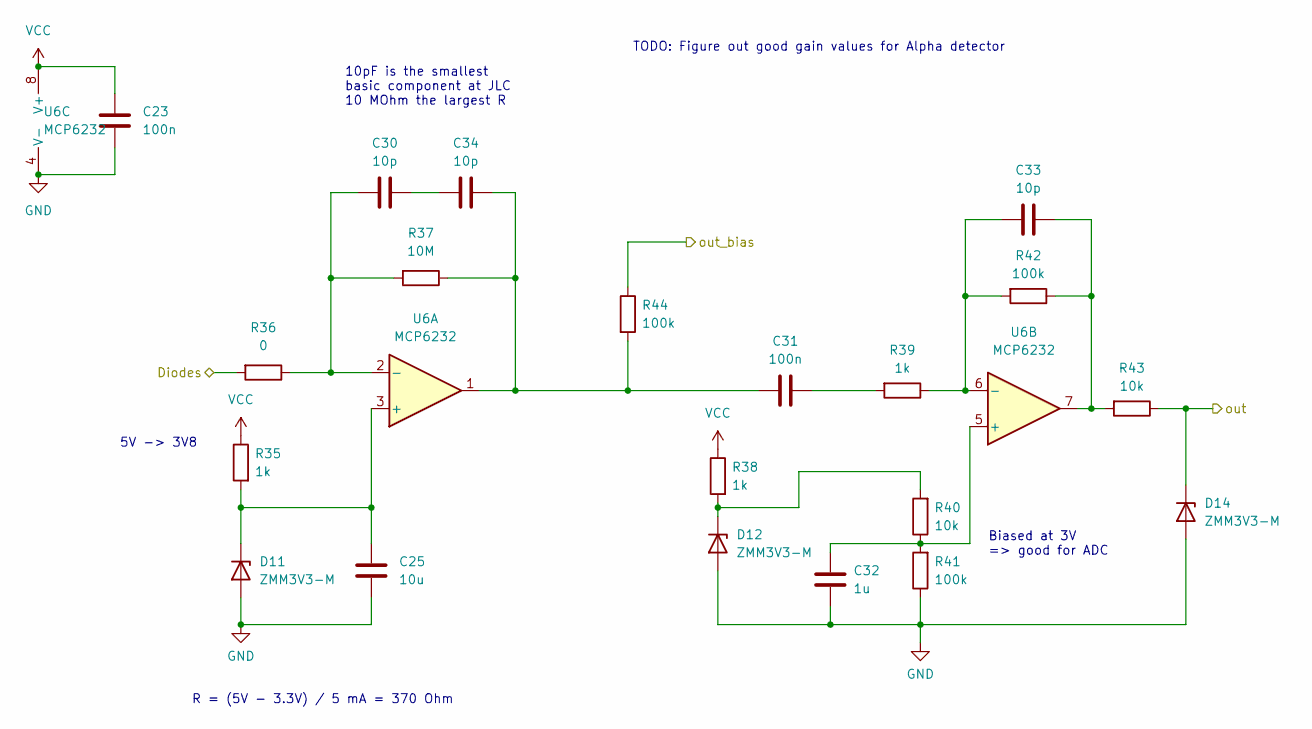
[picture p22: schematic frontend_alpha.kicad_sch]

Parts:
C23, C31: 100n; C_0603_1608Metric
C25: 10u; C_0603_1608Metric
C30, C33, C34: 10p; C_0603_1608Metric
C32: 1u; C_0603_1608Metric
D11, D12, D14: ZMM3V3-M; D_MiniMELF
R35, R38, R39: 1k; R_0603_1608Metric
R36: 0; R_0603_1608Metric
R37: 10M; R_0603_1608Metric
R40, R43: 10k; R_0603_1608Metric
R41, R42, R44: 100k; R_0603_1608Metric
U6: MCP6232; SOIC-8_3.9x4.9mm_P1.27mm

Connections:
/Frontend Alpha/Diodes: R36.2; also elsewhere on the board
/Frontend Alpha/out: D14.1 (K), R43.1; also elsewhere on the board
/Frontend Alpha/out_bias: R44.1; also elsewhere on the board
GND: C23.2, C25.2, C32.2, D11.2 (A), D12.2 (A), D14.2 (A), R41.1, U6.4 (V-); also elsewhere on the board
unnamed: C30.2, C34.1
unnamed: C31.1, C34.2, R37.1, R44.2, U6.1
unnamed: C31.2, R39.2
unnamed: C33.2, R42.1, R43.2, U6.7
unnamed: C25.1, D11.1 (K), R35.2, U6.3 (+)
unnamed: D12.1 (K), R38.2, R40.2
unnamed: C30.1, R36.1, R37.2, U6.2 (-)
unnamed: C32.1, R40.1, R41.2, U6.5 (+)
unnamed: C33.1, R39.1, R42.2, U6.6 (-)
VCC: C23.1, R35.1, R38.1, U6.8 (V+); also elsewhere on the board

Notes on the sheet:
5V -> 3V8
TODO: Figure out good gain values for Alpha detector
10pF is the smallest basic component at JLC 10 MOhm the largest R
R = (5V - 3.3V) / 5 mA = 370 Ohm
Biased at 3V => good for ADC

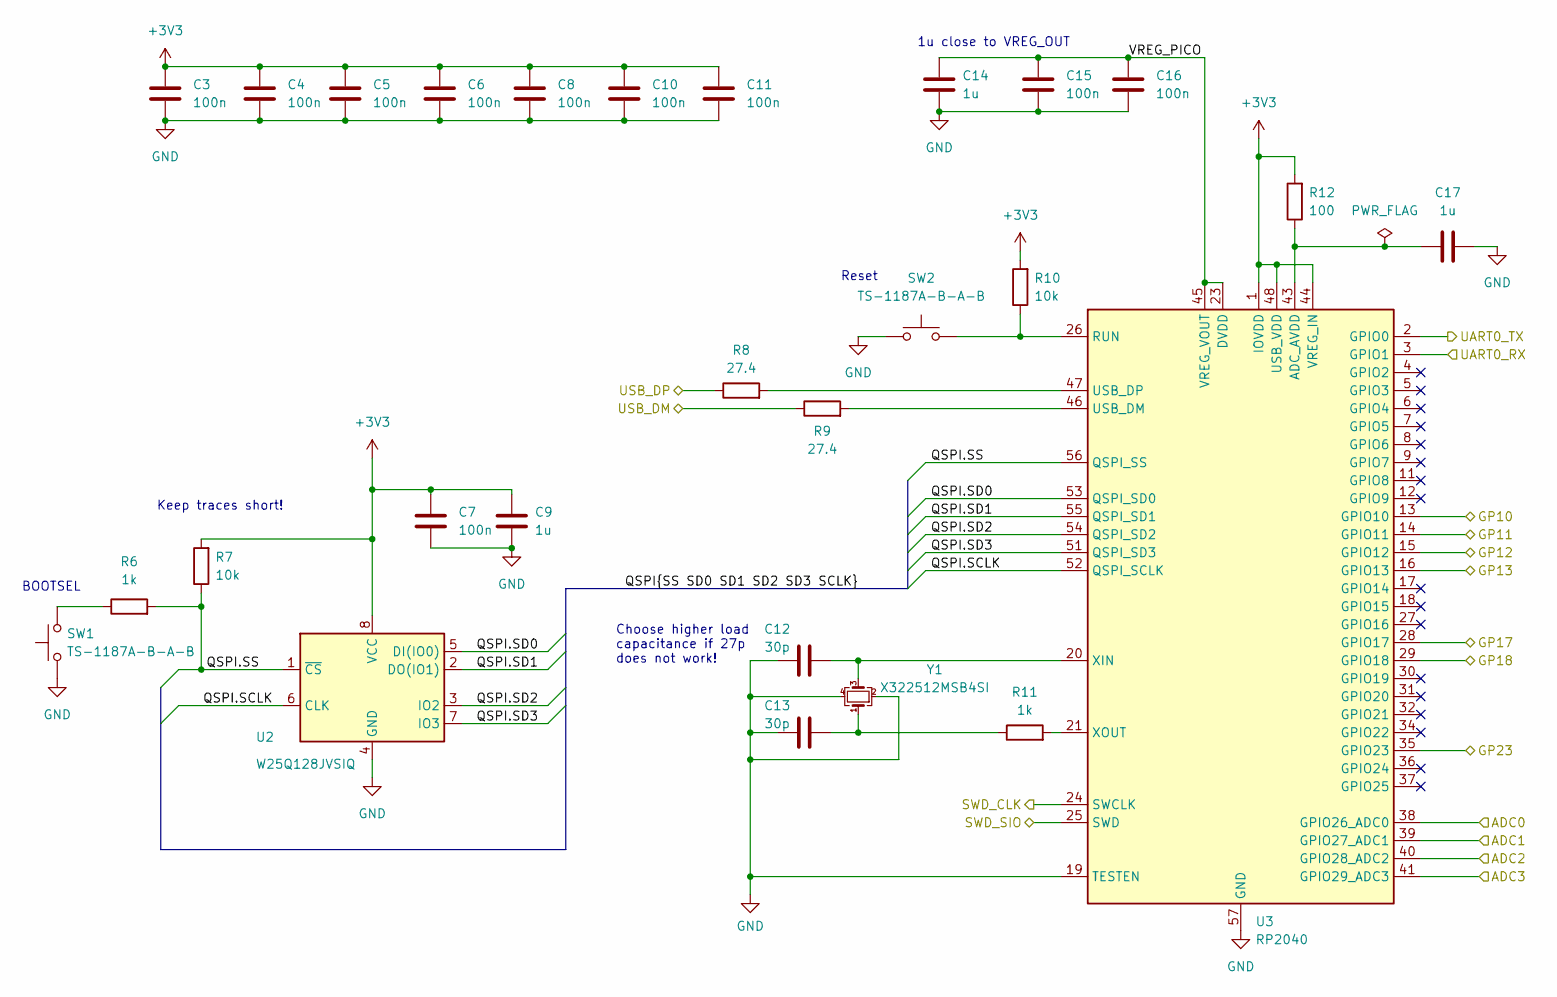
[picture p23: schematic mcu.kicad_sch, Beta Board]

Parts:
C3, C4, C5, C6, C7, C8, C10, C11, C15, C16: 100n; C_0603_1608Metric
C9, C14, C17: 1u; C_0603_1608Metric
C12, C13: 30p; C_0603_1608Metric
R6, R11: 1k; R_0603_1608Metric
R7, R10: 10k; R_0603_1608Metric
R8, R9: 27.4; R_0603_1608Metric
R12: 100; R_0603_1608Metric
SW1, SW2: TS-1187A-B-A-B
U2: W25Q128JVSIQ; SOIC-8_5.23x5.23mm_P1.27mm
U3: RP2040; QFN-56-1EP_7x7mm_P0.4mm_EP3.2x3.2mm
Y1: X322512MSB4SI; Crystal_SMD_3225-4Pin_3.2x2.5mm

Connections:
+3V3: C3.1, C4.1, C5.1, C6.1, C7.1, C8.1, C9.1, C10.1, C11.1, R7.2, R10.2, R12.2, U2.8 (VCC), U3.1 (IOVDD), U3.10 (IOVDD), U3.22 (IOVDD), U3.33 (IOVDD), U3.42 (IOVDD), U3.44 (VREG_IN), U3.48 (USB_VDD), U3.49 (IOVDD); also elsewhere on the board
/Frontend Alpha/out: U3.38 (GPIO26_ADC0); also elsewhere on the board
/Frontend Alpha/out_bias: U3.35 (GPIO23); also elsewhere on the board
/MCU/ADC1: U3.39 (GPIO27_ADC1); also elsewhere on the board
/MCU/ADC2: U3.40 (GPIO28_ADC2); also elsewhere on the board
/MCU/ADC3: U3.41 (GPIO29_ADC3); also elsewhere on the board
/MCU/GP10: U3.13 (GPIO10); also elsewhere on the board
/MCU/GP11: U3.14 (GPIO11); also elsewhere on the board
/MCU/GP12: U3.15 (GPIO12); also elsewhere on the board
/MCU/GP13: U3.16 (GPIO13); also elsewhere on the board
/MCU/GP17: U3.28 (GPIO17)
/MCU/GP18: U3.29 (GPIO18); also elsewhere on the board
/MCU/QSPI.SCLK: U2.6 (CLK), U3.52 (QSPI_SCLK)
/MCU/QSPI.SD0: U2.5 (DI(IO0)), U3.53 (QSPI_SD0)
/MCU/QSPI.SD1: U2.2 (DO(IO1)), U3.55 (QSPI_SD1)
/MCU/QSPI.SD2: U2.3 (IO2), U3.54 (QSPI_SD2)
/MCU/QSPI.SD3: U2.7 (IO3), U3.51 (QSPI_SD3)
/MCU/QSPI.SS: R6.2, R7.1, U2.1 (~CS), U3.56 (QSPI_SS)
/MCU/SWD_CLK: U3.24 (SWCLK); also elsewhere on the board
/MCU/SWD_SIO: U3.25 (SWD); also elsewhere on the board
/MCU/UART0_RX: U3.3 (GPIO1); also elsewhere on the board
/MCU/UART0_TX: U3.2 (GPIO0); also elsewhere on the board
/MCU/USB_DM: R9.1; also elsewhere on the board
/MCU/USB_DP: R8.1; also elsewhere on the board
/MCU/VREG_PICO: C14.1, C15.1, C16.1, U3.23 (DVDD), U3.45 (VREG_VOUT), U3.50 (DVDD)
GND: C3.2, C4.2, C5.2, C6.2, C7.2, C8.2, C9.2, C10.2, C11.2, C12.1, C13.2, C14.2, C15.2, C16.2, C17.2, SW1.1, SW2.1, U2.4 (GND), U3.19 (TESTEN), U3.57 (GND), Y1.2, Y1.4; also elsewhere on the board
unnamed: C13.1, R11.1, Y1.1
unnamed: R6.1, SW1.2
unnamed: C17.1, R12.1, U3.43 (ADC_AVDD)
unnamed: R10.1, SW2.2, U3.26 (RUN)
unnamed: R9.2, U3.46 (USB_DM)
unnamed: R8.2, U3.47 (USB_DP)
unnamed: C12.2, U3.20 (XIN), Y1.3
unnamed: R11.2, U3.21 (XOUT)

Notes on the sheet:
Choose higher load capacitance if 27p does not work!
Reset
Keep traces short!
1u close to VREG_OUT
BOOTSEL

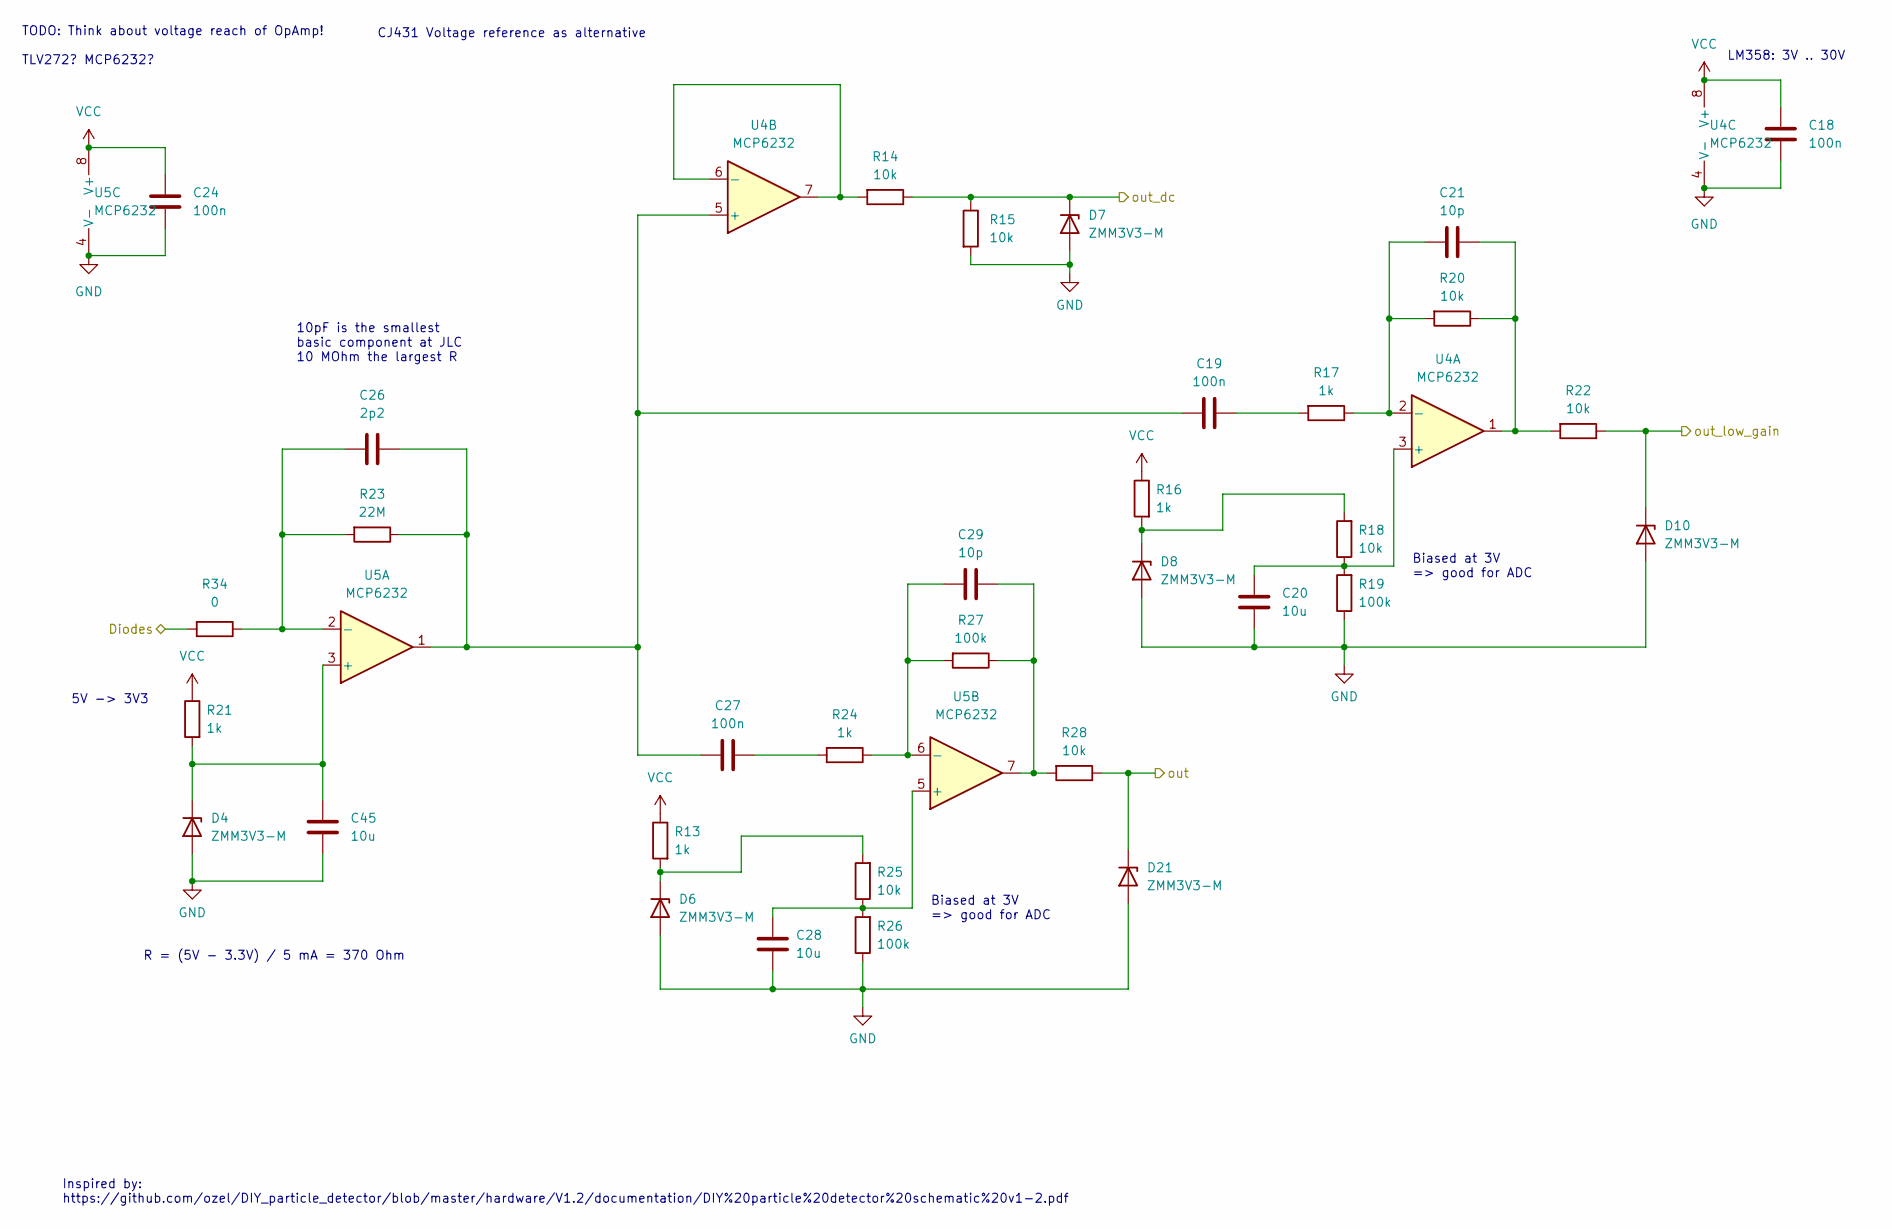
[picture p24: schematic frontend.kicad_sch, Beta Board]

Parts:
C18, C19, C24, C27: 100n; C_0603_1608Metric
C20, C28, C45: 10u; C_0603_1608Metric
C21, C29: 10p; C_0603_1608Metric
C26: 2p2; C_0603_1608Metric
D4, D6, D7, D8, D10, D21: ZMM3V3-M; D_MiniMELF
R13, R16, R17, R21, R24: 1k; R_0603_1608Metric
R14, R15, R18, R20, R22, R25, R28: 10k; R_0603_1608Metric
R19, R26, R27: 100k; R_0603_1608Metric
R23: 22M; R_0603_1608Metric
R34: 0; R_0603_1608Metric
U4, U5: MCP6232; SOIC-8_3.9x4.9mm_P1.27mm

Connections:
/MCU/ADC1: D10.1 (K), R22.1; also elsewhere on the board
/MCU/ADC2: D7.1 (K), R14.1, R15.1; also elsewhere on the board
/MCU/ADC3: D21.1 (K), R28.1; also elsewhere on the board
/particle_sensor_array1/Diodes: R34.2; also elsewhere on the board
GND: C18.2, C20.2, C24.2, C28.2, C45.2, D4.2 (A), D6.2 (A), D7.2 (A), D8.2 (A), D10.2 (A), D21.2 (A), R15.2, R19.1, R26.1, U4.4 (V-), U5.4 (V-); also elsewhere on the board
unnamed: C19.2, R17.2
unnamed: C21.2, R20.1, R22.2, U4.1
unnamed: C27.2, R24.2
unnamed: C29.2, R27.1, R28.2, U5.7
unnamed: C45.1, D4.1 (K), R21.2, U5.3 (+)
unnamed: D6.1 (K), R13.2, R25.2
unnamed: D8.1 (K), R16.2, R18.2
unnamed: C20.1, R18.1, R19.2, U4.3 (+)
unnamed: C21.1, R17.1, R20.2, U4.2 (-)
unnamed: C19.1, C26.2, C27.1, R23.1, U4.5 (+), U5.1
unnamed: R14.2, U4.6 (-), U4.7
unnamed: C26.1, R23.2, R34.1, U5.2 (-)
unnamed: C28.1, R25.1, R26.2, U5.5 (+)
unnamed: C29.1, R24.1, R27.2, U5.6 (-)
VCC: C18.1, C24.1, R13.1, R16.1, R21.1, U4.8 (V+), U5.8 (V+); also elsewhere on the board

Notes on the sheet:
Inspired by: https://github.com/ozel/DIY_particle_detector/blob/master/hardware/V1.2/documentation/DIY%20particle%20detector%20schematic%20v1-2.pdf
TODO: Think about voltage reach of OpAmp! TLV272? MCP6232?
5V -> 3V3
CJ431 Voltage reference as alternative
10pF is the smallest basic component at JLC 10 MOhm the largest R
Biased at 3V => good for ADC
R = (5V - 3.3V) / 5 mA = 370 Ohm
LM358: 3V .. 30V

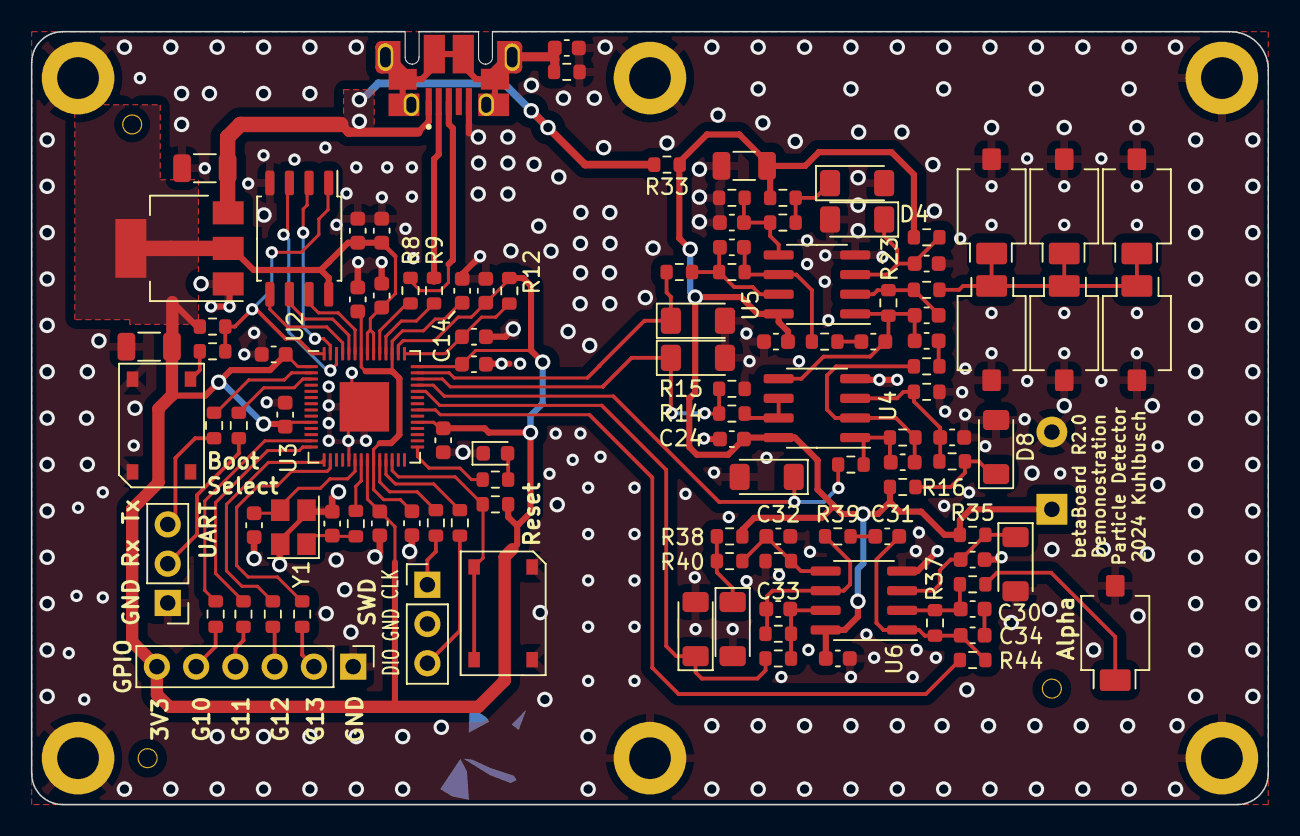
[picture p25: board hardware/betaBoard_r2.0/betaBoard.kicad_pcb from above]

Board: 2 copper layers, 80.0 x 50.0 mm, 121 parts (1 on the bottom side), 70 nets.

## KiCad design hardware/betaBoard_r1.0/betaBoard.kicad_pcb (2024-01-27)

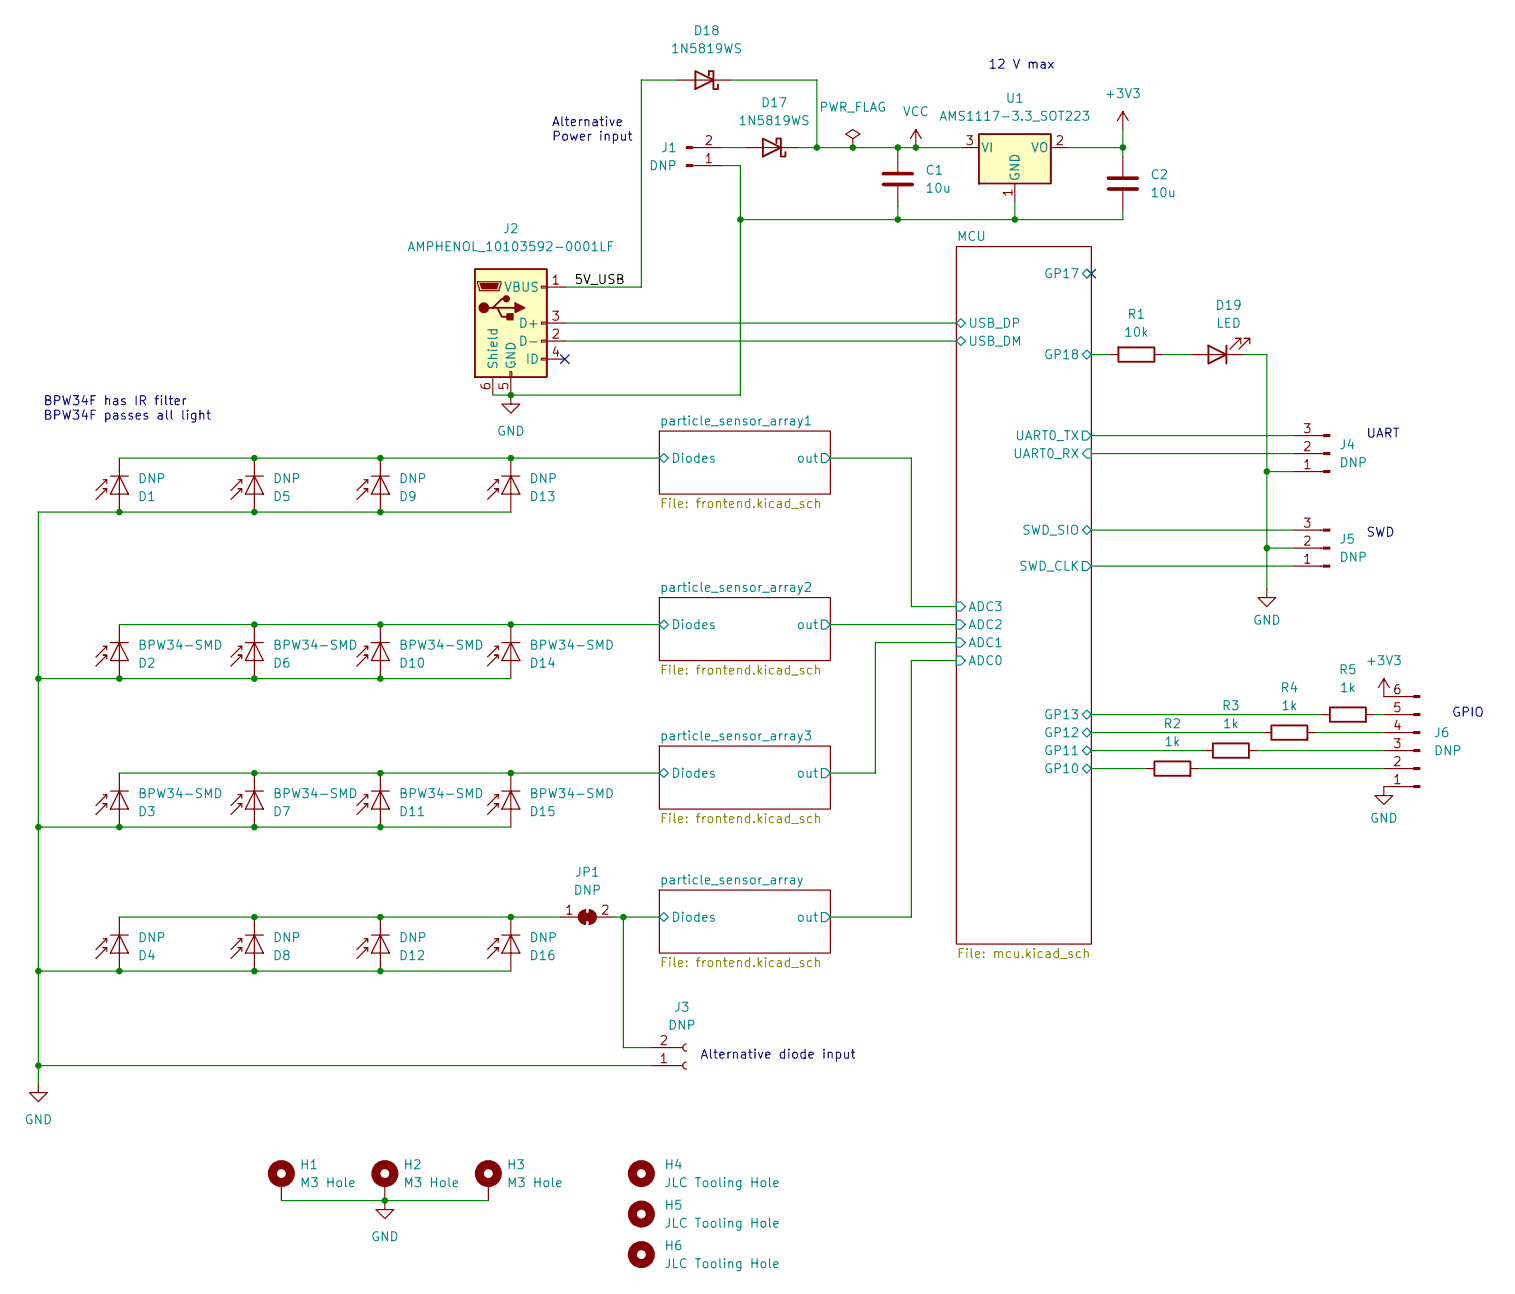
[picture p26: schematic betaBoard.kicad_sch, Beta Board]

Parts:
C1, C2: 10u; C_1206_3216Metric
D1, D4, D5, D8, D9, D12, D13, D16: DNP; Osram_BPW34S-SMD
D2, D3, D6, D7, D10, D11, D14, D15: BPW34-SMD; Osram_BPW34S-SMD_hole
D17, D18: 1N5819WS; D_SOD-323
D19: LED; LED_0603_1608Metric
H1, H2, H3: M3 Hole; MountingHole_2.7mm_M2.5_DIN965_Pad
H4, H5, H6: JLC Tooling Hole; JLC_tooling_hole
J1: DNP; PinHeader_1x02_P2.54mm_castellation
J2: AMPHENOL_10103592-0001LF
J3: DNP; PinSocket_1x02_P2.54mm_Vertical
J4, J5: DNP; PinHeader_1x03_P2.54mm_Vertical
J6: DNP; PinHeader_1x06_P2.54mm_Vertical
JP1: DNP; SolderJumper-2_P1.3mm_Bridged2Bar_Pad1.0x1.5mm
R1: 10k; R_0603_1608Metric
R2, R3, R4, R5: 1k; R_0603_1608Metric
U1: AMS1117-3.3_SOT223; SOT-223-3_TabPin2

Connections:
+3V3: C2.1, J6.6, U1.2 (VO); also elsewhere on the board
/5V_USB: D18.2 (A), J2.1 (VBUS)
/MCU/GP10: R2.1; also elsewhere on the board
/MCU/GP11: R3.1; also elsewhere on the board
/MCU/GP12: R4.1; also elsewhere on the board
/MCU/GP13: R5.1; also elsewhere on the board
/MCU/GP18: R1.2; also elsewhere on the board
/MCU/SWD_CLK: J5.1; also elsewhere on the board
/MCU/SWD_SIO: J5.3; also elsewhere on the board
/MCU/UART0_RX: J4.2; also elsewhere on the board
/MCU/UART0_TX: J4.3; also elsewhere on the board
/MCU/USB_DM: J2.2 (D-); also elsewhere on the board
/MCU/USB_DP: J2.3 (D+); also elsewhere on the board
/particle_sensor_array1/Diodes: D1.1 (K), D5.1 (K), D9.1 (K), D13.1 (K); also elsewhere on the board
/particle_sensor_array2/Diodes: D2.1 (K), D6.1 (K), D10.1 (K), D14.1 (K); also elsewhere on the board
/particle_sensor_array3/Diodes: D3.1 (K), D7.1 (K), D11.1 (K), D15.1 (K); also elsewhere on the board
/particle_sensor_array/Diodes: J3.2, JP1.2 (B); also elsewhere on the board
GND: C1.2, C2.2, D1.2 (A), D2.2 (A), D3.2 (A), D4.2 (A), D5.2 (A), D6.2 (A), D7.2 (A), D8.2 (A), D9.2 (A), D10.2 (A), D11.2 (A), D12.2 (A), D13.2 (A), D14.2 (A), D15.2 (A), D16.2 (A), D19.1 (K), H1.1, H2.1, H3.1, J1.1, J2.5 (GND), J2.6 (Shield), J3.1, J4.1, J5.2, J6.1, U1.1 (GND); also elsewhere on the board
unnamed: D4.1 (K), D8.1 (K), D12.1 (K), D16.1 (K), JP1.1 (A)
unnamed: D17.2 (A), J1.2
unnamed: D19.2 (A), R1.1
unnamed: J6.2, R2.2
unnamed: J6.3, R3.2
unnamed: J6.4, R4.2
unnamed: J6.5, R5.2
VCC: C1.1, D17.1 (K), D18.1 (K), U1.3 (VI); also elsewhere on the board

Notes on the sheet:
SWD
12 V max
Alternative Power input
Alternative diode input
GPIO
BPW34F has IR filter BPW34F passes all light
UART

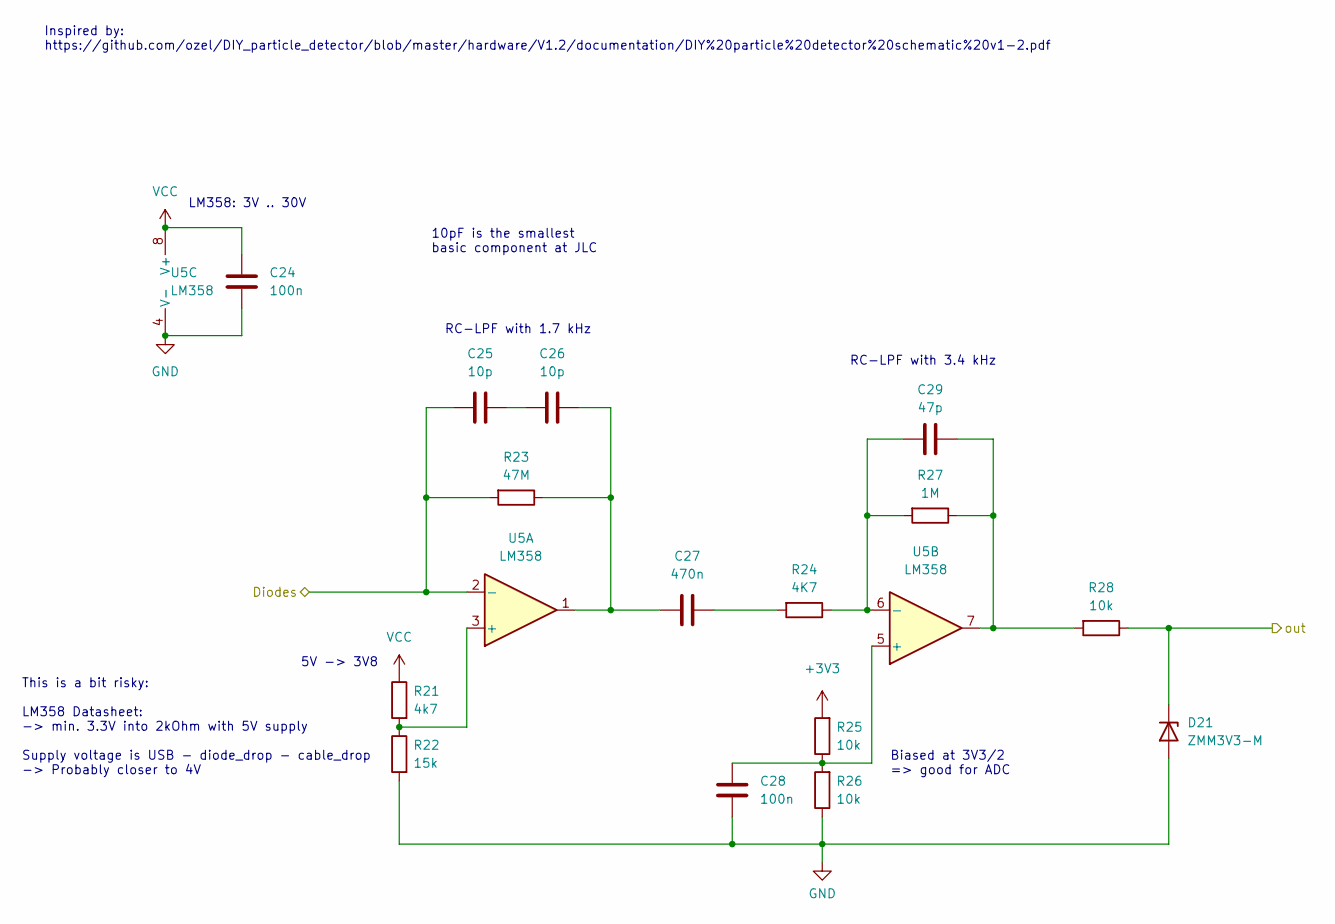
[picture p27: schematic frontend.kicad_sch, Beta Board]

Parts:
C24, C28: 100n; C_0603_1608Metric
C25, C26: 10p; C_0603_1608Metric
C27: 470n; C_0603_1608Metric
C29: 47p; C_0603_1608Metric
D21: ZMM3V3-M; D_MiniMELF
R21: 4k7; R_0603_1608Metric
R22: 15k; R_0603_1608Metric
R23: 47M; R_0603_1608Metric
R24: 4K7; R_0603_1608Metric
R25, R26, R28: 10k; R_0603_1608Metric
R27: 1M; R_0603_1608Metric
U5: LM358; SOIC-8_3.9x4.9mm_P1.27mm

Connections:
+3V3: R25.2; also elsewhere on the board
/MCU/ADC3: D21.1 (K), R28.1; also elsewhere on the board
/particle_sensor_array1/Diodes: C25.1, R23.2, U5.2 (-); also elsewhere on the board
GND: C24.2, C28.2, D21.2 (A), R22.2, R26.1, U5.4 (V-); also elsewhere on the board
unnamed: C25.2, C26.1
unnamed: C26.2, C27.1, R23.1, U5.1
unnamed: C27.2, R24.2
unnamed: C29.2, R27.1, R28.2, U5.7
unnamed: R21.2, R22.1, U5.3 (+)
unnamed: C28.1, R25.1, R26.2, U5.5 (+)
unnamed: C29.1, R24.1, R27.2, U5.6 (-)
VCC: C24.1, R21.1, U5.8 (V+); also elsewhere on the board

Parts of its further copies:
C18, C22, C30, C34, C36, C40: 100n; C_0603_1608Metric
C19, C20, C31, C32, C37, C38: 10p; C_0603_1608Metric
C21, C33, C39: 470n; C_0603_1608Metric
C23, C35, C41: 47p; C_0603_1608Metric
D20, D22, D23: ZMM3V3-M; D_MiniMELF
R13, R29, R37: 4k7; R_0603_1608Metric
R14, R30, R38: 15k; R_0603_1608Metric
R15, R31, R39: 47M; R_0603_1608Metric
R16, R32, R40: 4K7; R_0603_1608Metric
R17, R18, R20, R33, R34, R36, R41, R42, R44: 10k; R_0603_1608Metric
R19, R35, R43: 1M; R_0603_1608Metric
U4, U6, U7: LM358; SOIC-8_3.9x4.9mm_P1.27mm

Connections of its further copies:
+3V3: R17.2, R33.2, R41.2; also elsewhere on the board
/MCU/ADC0: D20.1 (K), R20.1; also elsewhere on the board
/MCU/ADC1: D23.1 (K), R44.1; also elsewhere on the board
/MCU/ADC2: D22.1 (K), R36.1; also elsewhere on the board
/particle_sensor_array2/Diodes: C31.1, R31.2, U6.2 (-); also elsewhere on the board
/particle_sensor_array3/Diodes: C37.1, R39.2, U7.2 (-); also elsewhere on the board
/particle_sensor_array/Diodes: C19.1, R15.2, U4.2 (-); also elsewhere on the board
GND: C18.2, C22.2, C30.2, C34.2, C36.2, C40.2, D20.2 (A), D22.2 (A), D23.2 (A), R14.2, R18.1, R30.2, R34.1, R38.2, R42.1, U4.4 (V-), U6.4 (V-), U7.4 (V-); also elsewhere on the board
unnamed: C19.2, C20.1
unnamed: C20.2, C21.1, R15.1, U4.1
unnamed: C21.2, R16.2
unnamed: C23.2, R19.1, R20.2, U4.7
unnamed: C31.2, C32.1
unnamed: C32.2, C33.1, R31.1, U6.1
unnamed: C33.2, R32.2
unnamed: C35.2, R35.1, R36.2, U6.7
unnamed: C37.2, C38.1
unnamed: C38.2, C39.1, R39.1, U7.1
unnamed: C39.2, R40.2
unnamed: C41.2, R43.1, R44.2, U7.7
unnamed: R13.2, R14.1, U4.3 (+)
unnamed: C22.1, R17.1, R18.2, U4.5 (+)
unnamed: C23.1, R16.1, R19.2, U4.6 (-)
unnamed: R29.2, R30.1, U6.3 (+)
unnamed: C34.1, R33.1, R34.2, U6.5 (+)
unnamed: C35.1, R32.1, R35.2, U6.6 (-)
unnamed: R37.2, R38.1, U7.3 (+)
unnamed: C40.1, R41.1, R42.2, U7.5 (+)
unnamed: C41.1, R40.1, R43.2, U7.6 (-)
VCC: C18.1, C30.1, C36.1, R13.1, R29.1, R37.1, U4.8 (V+), U6.8 (V+), U7.8 (V+); also elsewhere on the board

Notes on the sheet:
LM358: 3V .. 30V
RC-LPF with 3.4 kHz
Inspired by: https://github.com/ozel/DIY_particle_detector/blob/master/hardware/V1.2/documentation/DIY%20particle%20detector%20schematic%20v1-2.pdf
5V -> 3V8
RC-LPF with 1.7 kHz
10pF is the smallest basic component at JLC
Biased at 3V3/2 => good for ADC
This is a bit risky: LM358 Datasheet: -> min. 3.3V into 2kOhm with 5V supply Supply voltage is USB - diode_drop - cable_drop -> Probably closer to 4V

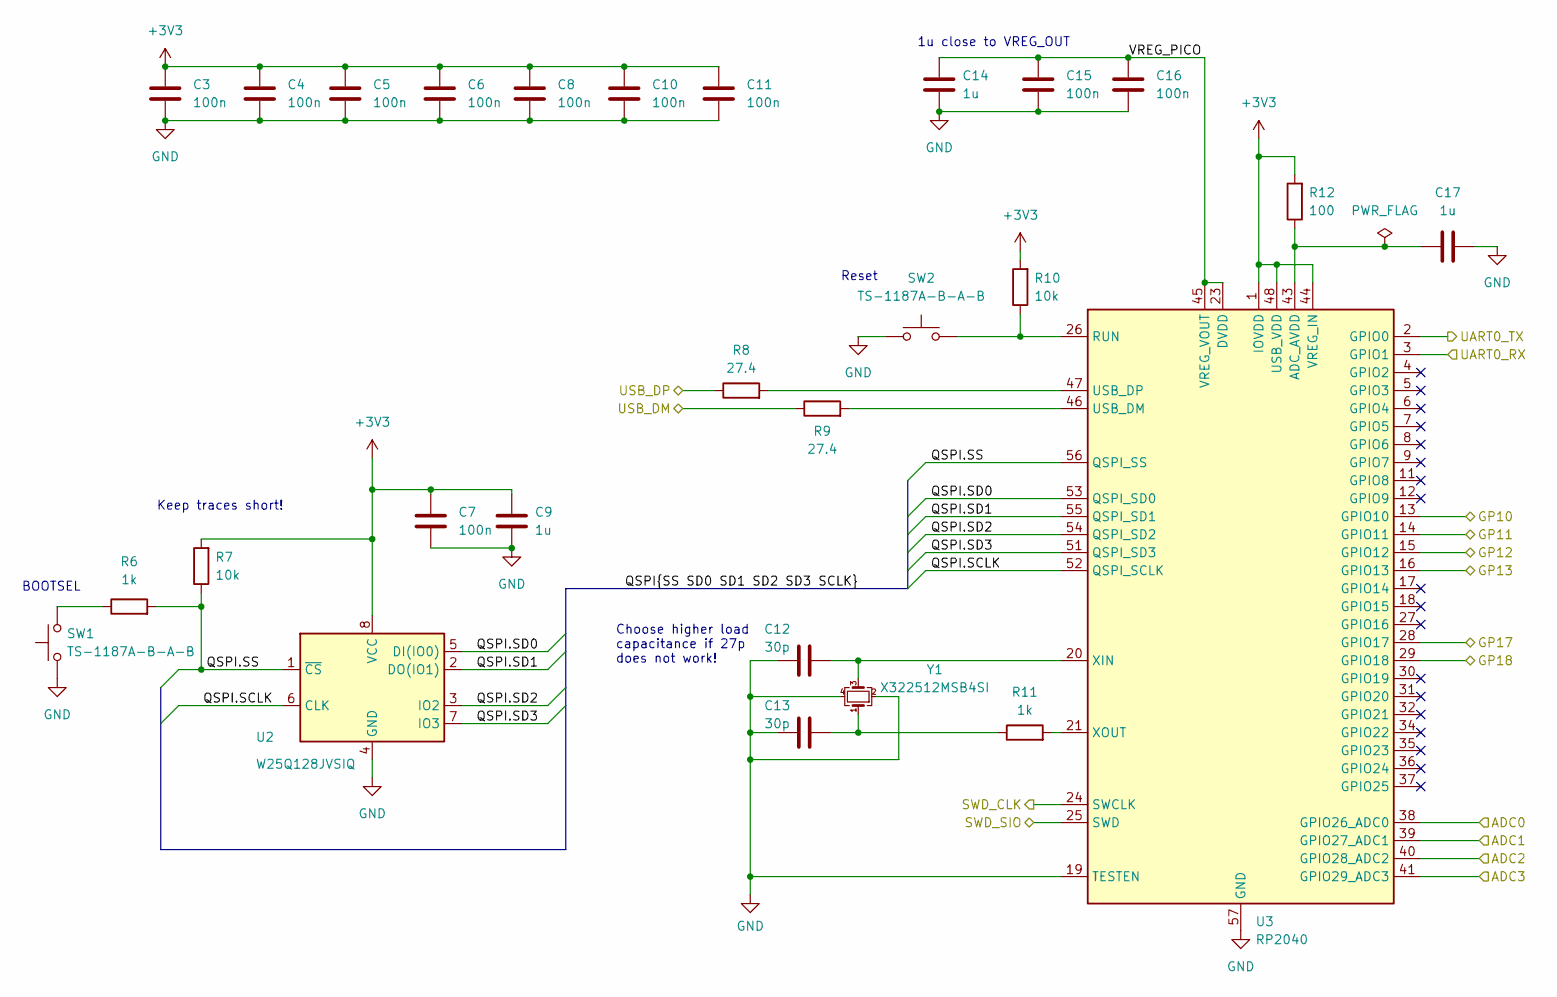
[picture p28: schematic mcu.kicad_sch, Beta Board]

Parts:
C3, C4, C5, C6, C7, C8, C10, C11, C15, C16: 100n; C_0603_1608Metric
C9, C14, C17: 1u; C_0603_1608Metric
C12, C13: 30p; C_0603_1608Metric
R6, R11: 1k; R_0603_1608Metric
R7, R10: 10k; R_0603_1608Metric
R8, R9: 27.4; R_0603_1608Metric
R12: 100; R_0603_1608Metric
SW1, SW2: TS-1187A-B-A-B
U2: W25Q128JVSIQ; SOIC-8_5.23x5.23mm_P1.27mm
U3: RP2040; QFN-56-1EP_7x7mm_P0.4mm_EP3.2x3.2mm
Y1: X322512MSB4SI; Crystal_SMD_3225-4Pin_3.2x2.5mm

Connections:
+3V3: C3.1, C4.1, C5.1, C6.1, C7.1, C8.1, C9.1, C10.1, C11.1, R7.2, R10.2, R12.2, U2.8 (VCC), U3.1 (IOVDD), U3.10 (IOVDD), U3.22 (IOVDD), U3.33 (IOVDD), U3.42 (IOVDD), U3.44 (VREG_IN), U3.48 (USB_VDD), U3.49 (IOVDD); also elsewhere on the board
/MCU/ADC0: U3.38 (GPIO26_ADC0); also elsewhere on the board
/MCU/ADC1: U3.39 (GPIO27_ADC1); also elsewhere on the board
/MCU/ADC2: U3.40 (GPIO28_ADC2); also elsewhere on the board
/MCU/ADC3: U3.41 (GPIO29_ADC3); also elsewhere on the board
/MCU/GP10: U3.13 (GPIO10); also elsewhere on the board
/MCU/GP11: U3.14 (GPIO11); also elsewhere on the board
/MCU/GP12: U3.15 (GPIO12); also elsewhere on the board
/MCU/GP13: U3.16 (GPIO13); also elsewhere on the board
/MCU/GP17: U3.28 (GPIO17)
/MCU/GP18: U3.29 (GPIO18); also elsewhere on the board
/MCU/QSPI.SCLK: U2.6 (CLK), U3.52 (QSPI_SCLK)
/MCU/QSPI.SD0: U2.5 (DI(IO0)), U3.53 (QSPI_SD0)
/MCU/QSPI.SD1: U2.2 (DO(IO1)), U3.55 (QSPI_SD1)
/MCU/QSPI.SD2: U2.3 (IO2), U3.54 (QSPI_SD2)
/MCU/QSPI.SD3: U2.7 (IO3), U3.51 (QSPI_SD3)
/MCU/QSPI.SS: R6.2, R7.1, U2.1 (~CS), U3.56 (QSPI_SS)
/MCU/SWD_CLK: U3.24 (SWCLK); also elsewhere on the board
/MCU/SWD_SIO: U3.25 (SWD); also elsewhere on the board
/MCU/UART0_RX: U3.3 (GPIO1); also elsewhere on the board
/MCU/UART0_TX: U3.2 (GPIO0); also elsewhere on the board
/MCU/USB_DM: R9.1; also elsewhere on the board
/MCU/USB_DP: R8.1; also elsewhere on the board
/MCU/VREG_PICO: C14.1, C15.1, C16.1, U3.23 (DVDD), U3.45 (VREG_VOUT), U3.50 (DVDD)
GND: C3.2, C4.2, C5.2, C6.2, C7.2, C8.2, C9.2, C10.2, C11.2, C12.1, C13.2, C14.2, C15.2, C16.2, C17.2, SW1.1, SW2.1, U2.4 (GND), U3.19 (TESTEN), U3.57 (GND), Y1.2, Y1.4; also elsewhere on the board
unnamed: C13.1, R11.1, Y1.1
unnamed: R6.1, SW1.2
unnamed: C17.1, R12.1, U3.43 (ADC_AVDD)
unnamed: R10.1, SW2.2, U3.26 (RUN)
unnamed: R9.2, U3.46 (USB_DM)
unnamed: R8.2, U3.47 (USB_DP)
unnamed: C12.2, U3.20 (XIN), Y1.3
unnamed: R11.2, U3.21 (XOUT)

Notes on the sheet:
Choose higher load capacitance if 27p does not work!
Reset
Keep traces short!
1u close to VREG_OUT
BOOTSEL

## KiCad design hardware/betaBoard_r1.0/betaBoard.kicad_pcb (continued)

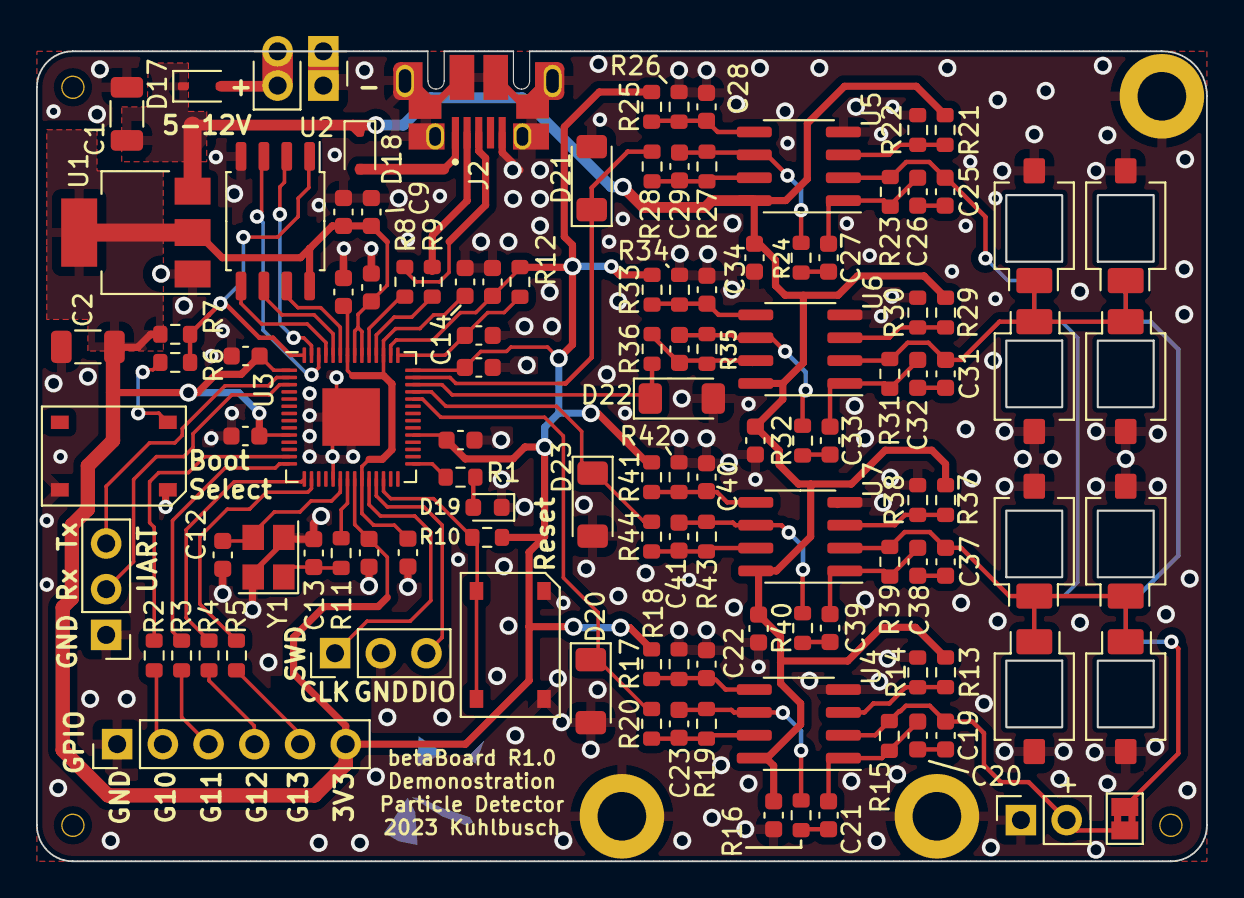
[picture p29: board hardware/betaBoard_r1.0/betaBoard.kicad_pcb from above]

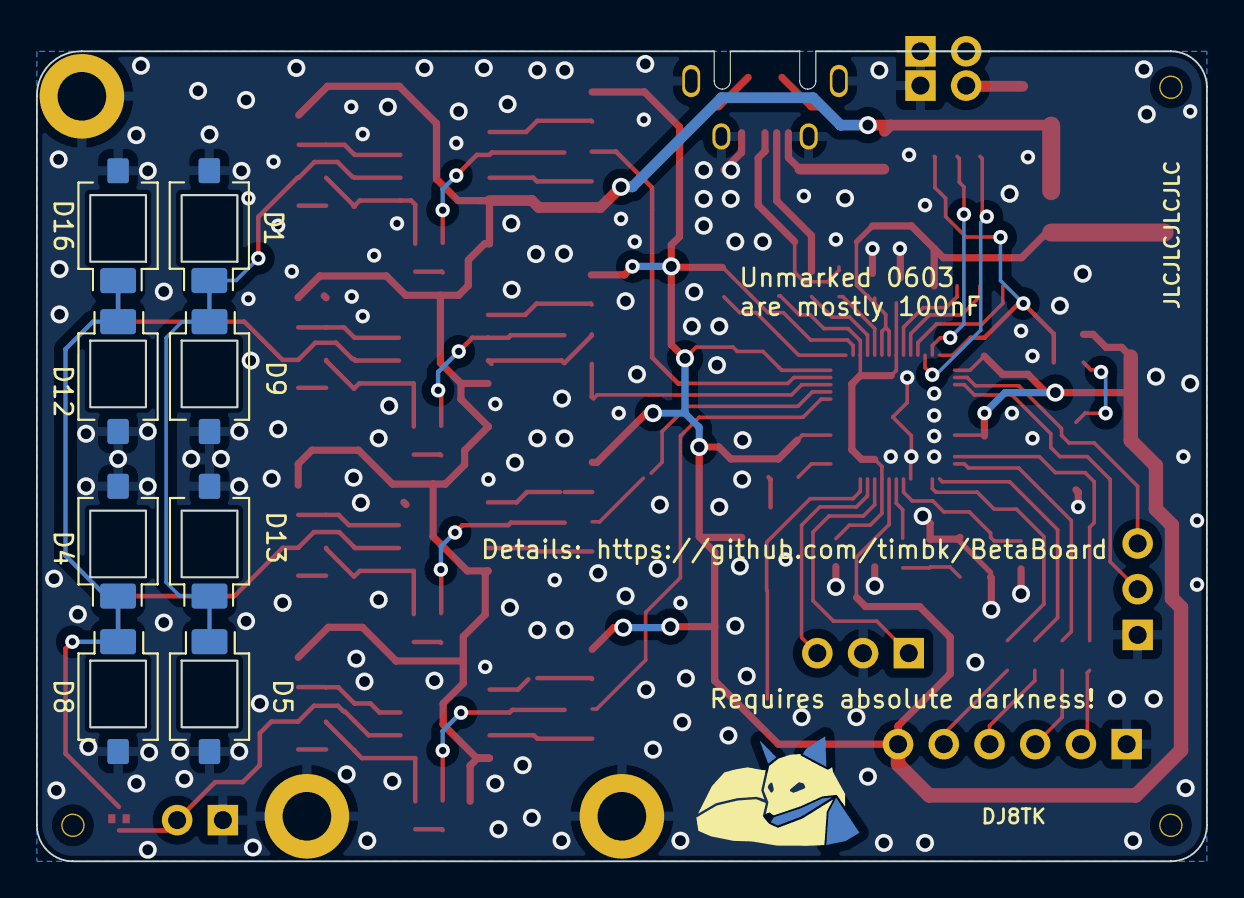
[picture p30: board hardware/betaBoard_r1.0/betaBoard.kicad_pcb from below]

Board: 2 copper layers, 65.0 x 45.0 mm, 131 parts (8 on the bottom side), 73 nets.

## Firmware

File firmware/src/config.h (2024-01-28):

#pragma once

// Pin definitions (not many for this PCB ;)
#define LED1_PIN 18
#define MAIN_LOOP_BLINK true

// The ADC channel to start reading from
#define DEFAULT_ADC_CHANNEL 2

// ADC rate config
#define ADC_RATE 500000 // ADC sample rate
#define ADC_CLOCK_DIV (48000000 / ADC_RATE - 1) // clock divider value, Brackets are important!
#define ADC_ACTUAL_RATE (48000000 / (ADC_CLOCK_DIV + 1)) // actual sample rate

// ADC buffer settings
#define ADC_BLOCK_SIZE (1024*20) // Buffer size, Brackets are important!!
#define ADC_QUEUE_MAX_SIZE 2 // buffer count
#define ADC_LEFTOVER_SIZE (64+128) // amount of samples that are stored to get full waveform readouts for triggers close to the block edge

// #define TRIGGER_THRESHOLD -0.045 // [V] 0.055 was the recommendattion for 9V operation
// #define TRIGGER_THRESHOLD -0.055 // [V] 0.055 was the recommendattion for 9V operation

#define USER_INPUT_BUFFER_SIZE 32
#define USER_INPUT_COMMIT_CHAR '\r'

#define BENCHMARK_BUFFER_SIZE (1024*8)
#define BENCHMARK_REPITITIONS 16

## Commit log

2023-12-28 add r1.0 design files
    [betaBoard.kicad_pcb, betaBoard.kicad_sch, bom.csv, designators.csv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]
2023-12-28 add schematic and PCB overview PDF
2023-12-28 add PDFs and production file update (no significant changes)
    [betaBoard.kicad_pcb, betaBoard.kicad_sch, bom.csv]
2024-01-09 final ordered R1.0 pcb
    [betaBoard.kicad_pcb, betaBoard.kicad_sch, bom.csv, designators.csv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]
2024-01-18 add image of R1.0 PCB
2024-01-24 add timestamps and overflow status to trigger waveform print
2024-01-27 move all hardware files to one folder
    [betaBoard.kicad_pcb, betaBoard.kicad_sch, bom.csv, designators.csv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]
2024-01-27 more moving of folders
    [betaBoard.kicad_pcb, betaBoard.kicad_sch, bom.csv, designators.csv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]
2024-01-27 add noise analysis script
    [amplifier_spice_sim.csv]
2024-01-28 move python interface to top level folder
    [amplifier_spice_sim.csv]
2024-01-28 python interface: add live plotting to main and read sample rate from device
2024-01-28 implement full waveform triggers on sample block edges
2024-02-04 start with r2.0
    [betaBoard.kicad_pcb, betaBoard.kicad_sch, frontend.kicad_sch, mcu.kicad_sch]
2024-02-07 main r2.0 design done
    [betaBoard.kicad_pcb, betaBoard.kicad_sch, frontend.kicad_sch, frontend_alpha.kicad_sch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]
2024-02-07 add r2.0 mid panel pcb
    [mid_panel_r2.0.kicad_pcb, mid_panel_r2.0.kicad_sch]
2024-02-07 add top panel pcb
    [top_panel_r2.0.kicad_pcb, top_panel_r2.0.kicad_sch]
2024-03-13 add command to disable blinking led
2024-07-31 python interface: record more information about the used board and configuration
2024-07-31 hardware: add new mid panel to make the device look nicer
    [mid_panel_r2.0.kicad_pcb, mid_panel_r2.0.kicad_sch]
2024-07-31 hardware: updated kicad version
    [betaBoard.kicad_pcb, betaBoard.kicad_sch, frontend.kicad_sch, frontend_alpha.kicad_sch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]
